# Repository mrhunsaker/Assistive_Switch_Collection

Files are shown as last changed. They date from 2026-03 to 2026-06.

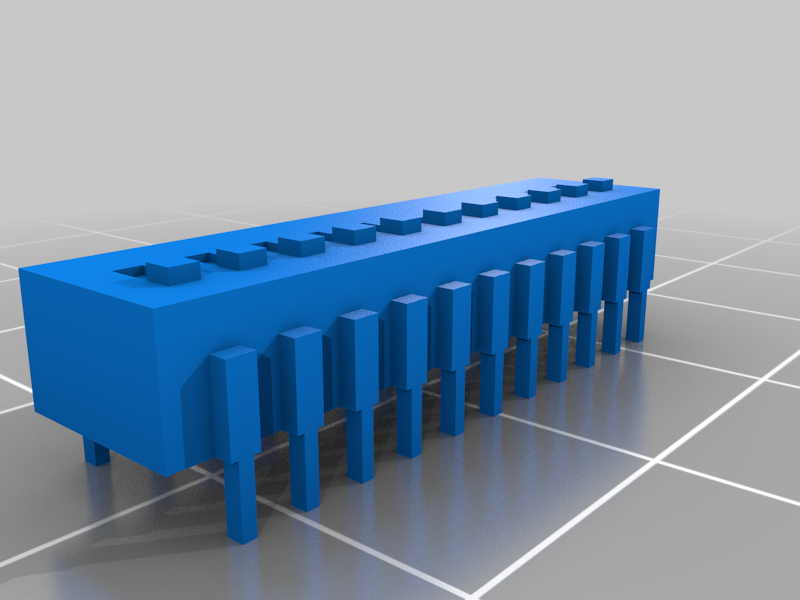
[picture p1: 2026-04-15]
TOSORT/DIP SWITCH, PUSH BUTTON, LED ELECTRONICS STL SPACE MODELS - 806060/images/2058_DIP_SWITCH.png

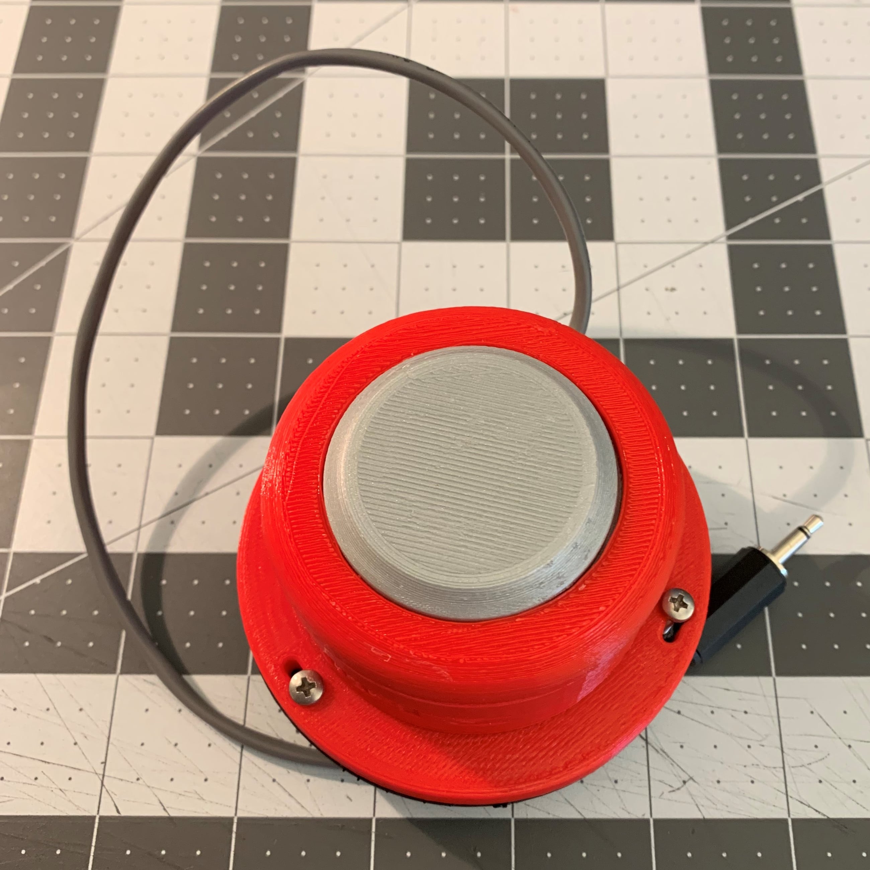
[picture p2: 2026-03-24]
switches/atmakers/AT Switch Remix - 3583410/images/Print_Assembled.jpg

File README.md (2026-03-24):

# Assistive Switch Collection

This repository is a curated collection of open‑source assistive **switches** and **switch interfaces**, collected as Git submodules and indexed in a machine‑readable CSV file.

The goal is to make it easier for clinicians, AT professionals, and makers to discover, compare, and build on existing open hardware.

---

## Repository structure

- `switch_projects.csv` — master index of projects (name, repo URL, type, number of inputs, IO mode, license, and whether 3D models are available).  
- `repos/` — Git submodules pointing at each upstream project.  
- `docs/` (optional) — any generated site or additional documentation.

---

## Project metadata fields

Each row in `switch_projects.csv` uses the following columns:

- `name` — human‑readable project name.  
- `github_repo` — canonical repository URL or project page if the code is linked from there.  
- `type` — one of:
  - `switch` for physical access switches (typically 3.5 mm).  
  - `interface` for devices that turn one or more switches (or sip‑and‑puff) into USB HID, gamepad, network, or relay outputs.  
  - `switch_controlled_device` for projects where the main goal is controlling something else (e.g., coffee maker, water pump) with an assistive switch.  
- `inputs` — approximate number and type of user inputs (e.g., `1`, `2`, `2+ sip_puff`).  
- `io_mode` — how the device presents itself or actuates:
  - `USB_HID`, `Bluetooth_HID`, `relay`, `network_to_servo`, `contact_closure`, etc.  
- `license` — SPDX identifier or short description (e.g., `MIT`, `CC-BY-NC-SA 4.0`).  
- `has_3d_files` — `yes` / `no` / `unknown`.  
- `notes` — brief free‑text description, special features, or caveats (e.g., non‑commercial license, requires specific microcontroller).

---

## Adding a new project

1. **Add the submodule**

   ```bash
   git submodule add https://github.com/USER/REPO.git repos/REPO
<!-- SUBMODULES:START -- auto-generated by add_submodules.sh, do not edit this block manually -->
## Submodules

This repository contains **48** submodule(s) organized by source.

To initialize after cloning:

```bash
git submodule update --init --recursive
```

### MMC: Physical Switches

| Repository | Path | Description |
|---|---|---|
| [`Chatterbox`](https://github.com/makersmakingchange/Chatterbox.git) | `switches/mmc/Chatterbox` | A switch scanning AAC device for users with visual impairment. |
| [`Lift-Switch`](https://github.com/makersmakingchange/Lift-Switch.git) | `switches/mmc/Lift-Switch` | A Switch Modifier that enables a switch to be activated when the switch is released rather than when pressed. |
| [`MMC60_Assistive_Switch`](https://github.com/makersmakingchange/MMC60_Assistive_Switch.git) | `switches/mmc/MMC60_Assistive_Switch` | A robust, 3D printable assistive switch with a 3.5 mm cable and easily swappable tops. |
| [`Twitch-Switch`](https://github.com/makersmakingchange/Twitch-Switch.git) | `switches/mmc/Twitch-Switch` | The Twitch Switch allows you to activate up to 3 switch adapted devices, or emulate a mouse or keyboard with movement as subtle as twitching your eyebrow. |
| [`Light-Proximity-Switch`](https://github.com/makersmakingchange/Light-Proximity-Switch.git) | `switches/mmc/Light-Proximity-Switch` | An open-source assistive switch that is activated by movement or extremely light contact. |
| [`Open-Wobble-Switch`](https://github.com/makersmakingchange/Open-Wobble-Switch.git) | `switches/mmc/Open-Wobble-Switch` | A cost effective wobble switch. This mountable assistive switch can be activated by moving the wand in any direction. |
| [`Interact-Switch`](https://github.com/makersmakingchange/Interact-Switch.git) | `switches/mmc/Interact-Switch` | An open source, 3D printable assistive switch with multiple topper options. |
| [`Big_Open_Switch`](https://github.com/makersmakingchange/Big_Open_Switch.git) | `switches/mmc/Big_Open_Switch` | A 3D printable assistive switch with a diameter of 150 mm |
| [`foot-pedal-switch`](https://github.com/makersmakingchange/foot-pedal-switch.git) | `switches/mmc/foot-pedal-switch` | A modified commercial foot pedal switch for use as an assistive switch |
| [`Open-Rocker-Switch`](https://github.com/makersmakingchange/Open-Rocker-Switch.git) | `switches/mmc/Open-Rocker-Switch` | An open source assistive switch activated by pressing down on either side or rocking the top relative to the base. |
| [`Round_Touch_60_Switch`](https://github.com/makersmakingchange/Round_Touch_60_Switch.git) | `switches/mmc/Round_Touch_60_Switch` | The Round Touch 60 Switch can control 3.5 mm audio outputs like in the Xbox Adaptive Controller and other switch adapted products.  |
| [`Raindrop-Switch`](https://github.com/makersmakingchange/Raindrop-Switch.git) | `switches/mmc/Raindrop-Switch` | A small, pressure-activated assistive switch |
| [`Resistive-Touch-Switch`](https://github.com/makersmakingchange/Resistive-Touch-Switch.git) | `switches/mmc/Resistive-Touch-Switch` | An open source assistive switch activated by minimal force skin contact. |
| [`Light-Touch-Switch`](https://github.com/makersmakingchange/Light-Touch-Switch.git) | `switches/mmc/Light-Touch-Switch` | A slim, pressure activated assistive switch with a 3.5 mm connection. |
| [`Wearable-Clap-Switch`](https://github.com/makersmakingchange/Wearable-Clap-Switch.git) | `switches/mmc/Wearable-Clap-Switch` | A wearable wireless switch that detects clap motion and activates an assistive device. |
| [`Finger-Lift-Switch`](https://github.com/makersmakingchange/Finger-Lift-Switch.git) | `switches/mmc/Finger-Lift-Switch` | An open-source assistive switch that can be activated by small lifting motions of a finger. |
| [`Hand-Raiser`](https://github.com/makersmakingchange/Hand-Raiser.git) | `switches/mmc/Hand-Raiser` | An assistive device used to catch the attention of a professor: an alternative to a student having to raise their hand. |
| [`Low-Profile-Switch`](https://github.com/makersmakingchange/Low-Profile-Switch.git) | `switches/mmc/Low-Profile-Switch` | A 3D printable, low profile assistive switch |
| [`Solderless-Unibody-Switch`](https://github.com/makersmakingchange/Solderless-Unibody-Switch.git) | `switches/mmc/Solderless-Unibody-Switch` | A solderless unibody assistive switch |
| [`Assistive-Switches-Kit`](https://github.com/makersmakingchange/Assistive-Switches-Kit.git) | `switches/mmc/Assistive-Switches-Kit` | An assortment of DIY 3d printable assistive switches. |
| [`Sip-And-Puff-Analog-Switch`](https://github.com/makersmakingchange/Sip-And-Puff-Analog-Switch.git) | `switches/mmc/Sip-And-Puff-Analog-Switch` | An open source analog sip and puff assistive switch |

### MMC: Switch Modifiers / Adapters

| Repository | Path | Description |
|---|---|---|
| [`Switch-Modifier`](https://github.com/makersmakingchange/Switch-Modifier.git) | `switches/mmc/Switch-Modifier` | An open assistive technology for modifying the output of an assistive switch |
| [`OpenAT-Switch-Latch`](https://github.com/makersmakingchange/OpenAT-Switch-Latch.git) | `switches/mmc/OpenAT-Switch-Latch` | An Open Assistive Technology device that adds latching functionality to an assistive switch. |
| [`Switch-Adapter-DualMono-Stereo`](https://github.com/makersmakingchange/Switch-Adapter-DualMono-Stereo.git) | `switches/mmc/Switch-Adapter-DualMono-Stereo` | Adapter for connecting two assistive switches to a single stereo input. |

### MMC: Switch Interfaces / Testers

| Repository | Path | Description |
|---|---|---|
| [`USB-Switch-Tester`](https://github.com/makersmakingchange/USB-Switch-Tester.git) | `switches/mmc/USB-Switch-Tester` | A DIY open source hardware device to test if an assistive switch is functional. |
| [`Simple-Switch-Tester`](https://github.com/makersmakingchange/Simple-Switch-Tester.git) | `switches/mmc/Simple-Switch-Tester` | A simple battery operated tester with a light for testing assistive switches via a 3.5 mm jack. |
| [`Shrub-Hub`](https://github.com/makersmakingchange/Shrub-Hub.git) | `switches/mmc/Shrub-Hub` | A low cost, easy to build digital switch interface for up to three assistive switches |
| [`Trinkey-Assistive-Interface`](https://github.com/makersmakingchange/Trinkey-Assistive-Interface.git) | `switches/mmc/Trinkey-Assistive-Interface` | A simple to build cost-effective assistive interface for digital access based on the Adafruit TRRS Trinkey. |
| [`Playback-Switch`](https://github.com/makersmakingchange/Playback-Switch.git) | `switches/mmc/Playback-Switch` | The Playback Switch is an assistive switch that also plays a prerecorded message up to 30 seconds long when the button is pressed.  |
| [`Single-Message-Playback-Switch`](https://github.com/makersmakingchange/Single-Message-Playback-Switch.git) | `switches/mmc/Single-Message-Playback-Switch` | Guide for modifying commercial message playback to work with external assistive switch. |
| [`Rocket-Switch-Interface`](https://github.com/makersmakingchange/Rocket-Switch-Interface.git) | `switches/mmc/Rocket-Switch-Interface` | A cost-effective two input switch interface based on a commercially available Trinkey board. |

### MMC: Wireless

| Repository | Path | Description |
|---|---|---|
| [`Wireless-Assistive-Swith-Link`](https://github.com/makersmakingchange/Wireless-Assistive-Swith-Link.git) | `switches/mmc/Wireless-Assistive-Switch-Link` | A wireless link between a 3.5 mm switch and an output device that has a 3.5 mm jack |
| [`wireless-assistive-switch-link`](https://github.com/makersmakingchange/wireless-assistive-switch-link.git) | `switches/mmc/wireless-assistive-switch-link` | Provides a way to wirelessly connect an assistive switch to a switch-adapted output device. |

### MMC: Mounting / Accessories

| Repository | Path | Description |
|---|---|---|
| [`Open_Universal_Mounting_Plate`](https://github.com/makersmakingchange/Open_Universal_Mounting_Plate.git) | `switches/mmc/Open_Universal_Mounting_Plate` | A simple 3d printed mount for assistive technology. Provides a flat surface for attaching AT using hook and loop fastener. Has a 1/4-20 UNC for compatibility with camera mounting options. |
| [`USB-Switcher-Modification`](https://github.com/makersmakingchange/USB-Switcher-Modification.git) | `switches/mmc/USB-Switcher-Modification` | This is a modification adds a switch jack input to the commercially available Sabrent USB 2.0 Sharing Switch, a device that allows a person to connect one USB device to two computers and switch between them. |
| [`Custom-Single-Switch-Kit`](https://github.com/makersmakingchange/Custom-Single-Switch-Kit.git) | `switches/mmc/Custom-Single-Switch-Kit` | An assistive switch that uses heat moldable polymer for a customized fit. |

### MMC: Sip-and-Puff Joysticks

| Repository | Path | Description |
|---|---|---|
| [`LipSync`](https://github.com/makersmakingchange/LipSync.git) | `switches/mmc/LipSync` | An open-source mouth operated sip and puff joystick that enables people with limited hand function to emulate a mouse on their computer and/or smartphone. |
| [`LipSync-Macro`](https://github.com/makersmakingchange/LipSync-Macro.git) | `switches/mmc/LipSync-Macro` | A mouth controlled open assistive technology alternative input device. |

### AsTeRICS

| Repository | Path | Description |
|---|---|---|
| [`buttondesigns`](https://github.com/asterics/buttondesigns) | `switches/asterics/buttondesigns` | Various 3D printed switch acuators for assistive input |
| [`FLipMouse`](https://github.com/asterics/FLipMouse) | `switches/asterics/FLipMouse` | The repository for FLipMouse (Finger and LipMouse) |
| [`FLipMouse-v2`](https://github.com/asterics/FLipMouse-v2) | `switches/asterics/FLipMouse-v2` | FLipMouse Version 2 |
| [`FABI`](https://github.com/asterics/FABI) | `switches/asterics/FABI` | The repository for FABI (Flexible Assistive Button Interface) |

### MTurvey

| Repository | Path | Description |
|---|---|---|
| [`InteractSwitch`](https://github.com/mwturvey/InteractSwitch.git) | `switches/mturvey/InteractSwitch` | Designs for a set of assistive technology switches |

### Misc / Community

| Repository | Path | Description |
|---|---|---|
| [`accessible-switches`](https://github.com/a11yhood/accessible-switches) | `switches/misc/accessible-switches` |  |
| [`Accessible-Switch`](https://github.com/greenpanda111/Accessible-Switch) | `switches/misc/Accessible-Switch` | CAD files to construct an accessible switch |
| [`atat-switch`](https://github.com/musghz/atat-switch) | `switches/misc/atat-switch` | Open source accessibility switch based on mechanical keyboard switches |
| [`openSipPuff`](https://github.com/jasonwebb/openSipPuff) | `switches/misc/openSipPuff` | Simple, low-cost \ |
| [`Sip-N-Puff-Accessibility-Project`](https://github.com/trainslaw/Sip-N-Puff-Accessibility-Project) | `switches/misc/Sip-N-Puff-Accessibility-Project` |  |

<!-- SUBMODULES:END -->

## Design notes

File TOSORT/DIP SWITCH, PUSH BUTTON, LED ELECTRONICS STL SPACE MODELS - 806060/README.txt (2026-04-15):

DIP SWITCH, PUSH BUTTON, LED ELECTRONICS STL SPACE MODELS by bathrobotics on Thingiverse: https://www.thingiverse.com/thing:806060

Summary:
THESE ARE ACCURATE FOR THE PURPOSES I USE.  FEEL FREE TO DOWNLOAD THE .PK2 CREO ELEMENTS FILE AND MODIFY FOR YOUR NEEDS.  10 WAY DUAL INLINE SWITCH,  LED WITH LEGS,  PUSH BUTTON

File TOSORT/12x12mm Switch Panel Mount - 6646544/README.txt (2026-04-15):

12x12mm Switch Panel Mount by TuriSc on Thingiverse: https://www.thingiverse.com/thing:6646544

Summary:
This enclosure is designed for mounting standard 12x12mm tactile micro switches to panels.It requires a 20mm hole for installation.After inserting the switch with its cap on, attach the locking part to secure it in place.The design does not require any supports for printing.

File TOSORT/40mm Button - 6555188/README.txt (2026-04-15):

40mm Button by paedia on Thingiverse: https://www.thingiverse.com/thing:6555188

Summary:
Sturdy 40mm Button. The clever scissor mechanism evenly distributes the pressure across the entire contact surface. The built-in microswitch is reliably activated even when pressed in the corner. The button is very robust and can also be used as a foot switch.Assembly: First, snap the scissor parts onto the base, then insert the microswitch and snap on the cover.Additionally, you’ll need:1 standard 5A microswitch (Omron SS-5 F or similar)2 brass inserts (M3, 5mm)2 countersunk screws (M3, 6mm)

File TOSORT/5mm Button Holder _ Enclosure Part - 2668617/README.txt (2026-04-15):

5mm Button Holder / Enclosure Part by PrintedHuman on Thingiverse: https://www.thingiverse.com/thing:2668617

Summary:
Need to include buttons in your project or model? Just paste in this model and you are ready.This is the optimized result of testing and prototypes and it fits like a charm with the usual cheap 5 mm switch push buttons.You don't need to give credit if you use this part, but I would thank you if you did, just link to this page. Thanks!There are 2 models, one with and one without a seperator. The seperator is useful for making sure that solder or wires wont short circuit with eachother.Enjoy!PS. You can buy this buttons safely and cheap over here: https://www.banggood.com/100pcs-Mini-Micro-Momentary-Tactile-Tact-Switch-Push-Button-DIP-P4-Normally-Open-p-917570.html?p=BE271351829962016060(Those are also the buttons I used for prototyping and testing)

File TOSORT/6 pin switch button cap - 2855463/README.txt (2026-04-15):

6 pin switch button cap by matszwe02 on Thingiverse: https://www.thingiverse.com/thing:2855463

Summary:
This is a simple power switch cap

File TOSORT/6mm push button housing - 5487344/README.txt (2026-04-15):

6mm push button housing by ringo2k on Thingiverse: https://www.thingiverse.com/thing:5487344

Summary:
This is an enclosure for a 6mmx6mm push button. I like the cheap buttons because of the the nice "push feeling". I wanted to have a base, which I can use to put these buttons on electronics housings. You need to print 3 parts: The base - There you put in the button (bend the legs and solder cables to it upfront)The pin - This is the pin, place it on the buttonThe housing - Put everything in the housing (super glue it together)That's it!

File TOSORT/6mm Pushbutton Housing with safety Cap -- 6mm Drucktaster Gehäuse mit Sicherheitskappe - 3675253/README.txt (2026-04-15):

6mm Pushbutton Housing with safety Cap  --  6mm Drucktaster Gehäuse mit Sicherheitskappe by SolarGermany on Thingiverse: https://www.thingiverse.com/thing:3675253

Summary:
6mm Pushbutton Housing with safety Caphttps://www.ebay.de/itm/100PCS-6x6x6-mm-Miniature-Micro-Momentary-Tactile-Tact-Touch-Push-Button-Switch/132488686881?epid=633717124&amp;hash=item1ed8f0ed21:g:7DIAAOSwWlFbrzqw&amp;frcectupt=trueHave fun, like, and share you makes...SG.-.-.-.-.-.-.-.-.-.-.-.-.-.-.-.-.-.-.-.-.-.-.-.-.-.-.-.-.-.-.-.-.-.-.-.-.-.-.-.-.-.-.-.-.-.-.-.-.-.-.-.-.-.-.-.-.-.-.-.-.-.-.-.-.-.6mm Drucktaster Gehäuse mit Sicherheitskappehttps://www.ebay.de/itm/100PCS-6x6x6-mm-Miniature-Micro-Momentary-Tactile-Tact-Touch-Push-Button-Switch/132488686881?epid=633717124&amp;hash=item1ed8f0ed21:g:7DIAAOSwWlFbrzqw&amp;frcectupt=trueHabt Spass, liked, und teilt Eure Makes...SG

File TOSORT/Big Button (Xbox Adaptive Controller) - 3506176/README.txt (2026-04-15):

Big Button (Xbox Adaptive Controller) by gripuf on Thingiverse: https://www.thingiverse.com/thing:3506176

Summary:
This design is a big button for use with the Xbox Adaptive Controller (XAC). The part is made up of 3 seperate components: the top of the button case, the bottom of the button case, and the actual button that you press. These components are all available for download as stl and SolidWorks files. On the inside of the part, there is a square slota to hold a keyboard switch. We used Green Cherry MX Keyswitches (https://mechanicalkeyboards.com/shop/index.php?l=product_list&amp;c=48) so those will fit best into the square slot.We use zipties to secure the top and base of the switch together.

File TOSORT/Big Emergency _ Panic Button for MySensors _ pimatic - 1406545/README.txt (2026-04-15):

Big Emergency / Panic Button for MySensors / pimatic by MaxWinterstein on Thingiverse: https://www.thingiverse.com/thing:1406545

Summary:
Emergency Button This is some big Emergency Button. I use it with my HouseAutomation to control things and stuff. As button itself i use a black Cherry MX switch that i had laying around. Works nice :)When it was printed i thought a lower height would be great, so i added a 15mm/piece version. The version in the video is 30mm/piece.What you need to do it like me:all three printed partsCherry MX switch of your choice (i got mine from Conrad GermanyArduino NRF24L01+ Radiosome cablessome M3 Screws (M3x30+ should do fine)You can read more about that stuff here:Software i use pimatic.orgHardware i use mysensors.orgVideo: https://www.youtube.com/watch?v=jMr5voq1hkAI stole the idea for fixing the knob to the switch from ohagel. Thanks buddy, mine creation did not work as expected ;)Update v2I changed the plate thickness of the top part from 1mm to 1.5mm, that should make the Cherry Switch fit much better.Update v3I think using one cherry switch is great. But using 4 cherry switches is even four times greater. So i added a top and a knob that can handle 4 cherry switches. I made one, and it feels very good. Sadly yellow is empty, so mine is gray.Update v4Added CAD files. Please be nice, i am not that good at it.

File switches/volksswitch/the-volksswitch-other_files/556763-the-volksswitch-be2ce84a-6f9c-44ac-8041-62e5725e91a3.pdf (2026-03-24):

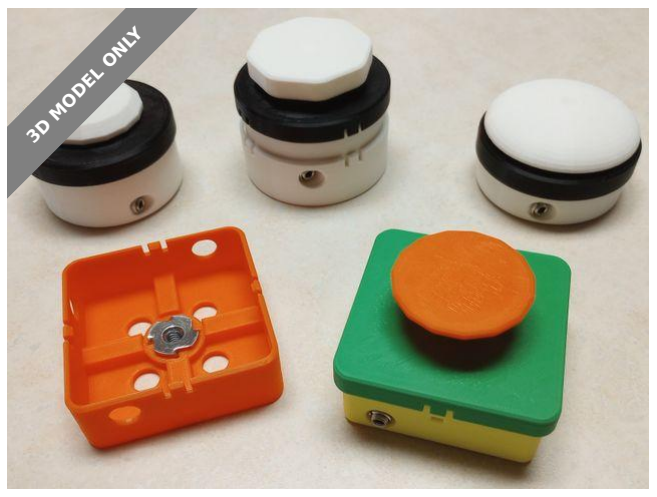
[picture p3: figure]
3D MODEL ONLY

## Summary

This pressure switch designer is highly customizable and requires no

soldering to assemble.

Hobby & Makers (https://printables.com/model?categoryId=48) | > | Electronics (https://printables.com/model?categoryId=52)
Tags: switch | customizable | assistivetech | assistivetechnology

This pressure switch designer allows you to customize the switch size,

shape, activation distance, activation force, and activation location. In

addition to a 3D-printed enclosure and activation surface, it uses off-the-

shelf parts that can be assembled using only a screwdriver. No Soldering

Necessary!

Instructions for using the switch designer can be found at the

Volksswitch.org website on this page:

https://volksswitch.org/index.php/volks-devices/the-volksswitch/

Volksswitch (https://printables.com/@Volksswitch_273749)

# The Volksswitch

VIEW IN BROWSER (https://printables.com/model/556763-the-volksswitch)

updated 26. 9. 2023 | published 26. 9. 2023

# Model files

# Other files

- remove the .txt part of the file name before expanding into a folder

## License

This work is licensed under a

Creative Commons (4.0 International License)

Attribution (http://creativecommons.org/licenses/by/4.0/)

✖ | Sharing without ATTRIBUTION
✔ | Remix Culture allowed
✔ | Commercial Use
✔ | Free Cultural Works
✔ | Meets Open Definition

the-volksswitch.scad

spacer-plug-matrix.pdf

evaluation_switch_stl_fileszip.txt

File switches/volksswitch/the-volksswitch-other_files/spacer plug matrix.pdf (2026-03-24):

activation force index | activation distance
0 | 1 | 2 | 3 | 4 | 5
0 | ?*
1 | 3.5 | 4.5 | 5.5 | 6.5 | 7.5 | 8.5
2 | 3.5 | 4.5 | 5.5 | 6.5 | 7.5 | 8.5
3 | 3 | 4 | 5 | 6 | 7 | 8
4 | 3 | 3.5 | 4.5 | 5.5 | 6.5 | 7.5
5 | 3 | 4 | 5 | 6 | 7 | 8
6 | 3 | 3 | 4 | 5 | 6 | 7
7 | 3 | 3.5 | 4.5 | 5.5 | 6.5 | 7.5
8 | 3 | 3 | 3.5 | 4.5 | 5.5 | 6.5
9 | 3 | 3 | 4 | 5 | 6 | 7
10 | 3 | 3 | 3.5 | 4.5 | 5.5 | 6.5
? = 6 for evaluation switches and 3 for standard switches
* = insert mini-post

not available
not available for 10 mm spacer

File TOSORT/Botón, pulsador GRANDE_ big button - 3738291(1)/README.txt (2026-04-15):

Botón, pulsador GRANDE/ big button by lafabricadepalabras on Thingiverse: https://www.thingiverse.com/thing:3738291

Summary:
Pulsador  (no interruptor)  de grandes dimensiones diseñado especialmente para personas con diversidad funcional. A éste se le conecta un cable jack para poder gobernar juguetes adaptados, dispositivos que faciliten el barrido en comunicadores, etc. Gracias a la gran labor de CEAPAT, con el diseño:https://www.thingiverse.com/thing:1096831

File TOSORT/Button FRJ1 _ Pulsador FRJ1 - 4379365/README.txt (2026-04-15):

Button FRJ1 / Pulsador FRJ1 by ceapat on Thingiverse: https://www.thingiverse.com/thing:4379365

Summary:
Switch designed for people with limited movement to operate communication equipment, toys and other electronic equipment.[Spanish] Pulsador doble de fácil accionamiento, para facilitar el acceso a otros productos adaptados para personas con movilidad reducida.Se puede utilizar con juguetes adaptados, mandos de TV, ratones y otros productos electrónicos adaptados.

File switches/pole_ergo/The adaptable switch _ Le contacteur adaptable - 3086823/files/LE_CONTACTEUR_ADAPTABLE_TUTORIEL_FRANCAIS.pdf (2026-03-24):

CC BY-NC-SA pole-ergo.fr - Guy Ehretsmann | 2018
www.pole-ergo.fr | technologie@pole-ergo.fr

LE CONTACTEUR ADAPTABLE

Guy Ehretsmann/Ergothérapeute

INTRODUCTION

Le contacteur est un bouton poussoir accessible très utilisé dans le domaine du handicap. Il est conçu pour faciliter l'accès à différents types de technologies et, de façon étendue, pour permettre à l'utilisateur d'agir sur son environnement.

Il transforme un geste moteur, manquant de précision, en, par exemple, un signal exploitable par un ordinateur, une tablette ou un téléphone pour les contrôler intégralement lorsqu'ils sont paramétrés pour ce mode de fonctionnement.

Le contacteur donne également l'accès à des jouets électriques, à des dispositifs de communications ou encore à des appareils pilotés par boutons tel que appareils photos, console de jeux, etc..

Les contacteurs sont disponibles dans le commerce spécialisé. On en trouve ainsi de différentes tailles, couleurs mais également de différents types et formes. Pourtant, le contacteur peut se révéler difficile à utiliser lorsque son design ne correspond pas au besoins spécifiques de l'utilisateur.

C'est la raison pour laquelle il peut s'avérer pertinent de disposer d'un contacteur adaptable que l'on pourra modifier en fonction des particularités motrices de l'utilisateur, de ses habitudes ou encore de ses goûts de façon à le rendre davantage accessible.

Le contacteur adaptable proposé ici offre une série de possibilités et d'options de personnalisations qui le rende potentiellement capable de répondre à toutes les situations.

Totalement imprimé à l'aide d'une imprimante 3D, les différentes pièces qui le composent s'assemblent comme des briques de Lego. Il offre différentes possibilités de fixations et de positionnement en exploitant la norme utilisée pour les minis caméras GOPRO, dont on trouve partout les accessoires à bas prix.

Il dispose également d'un bouton spécifique comportant des fixations à vis qui permet la fabrication et l'usage de boutons personnalisés et constitue, ainsi, une base pour la création de modèles uniques répondant à des besoins non génériques.

Enfin, l'assemblage du contacteur est facile et ne demande que deux soudures simples à l'étain qu'il est possible d'éviter, lorsque l'on ne dispose pas de fer à souder, en réalisant un simple sertissage de fils.

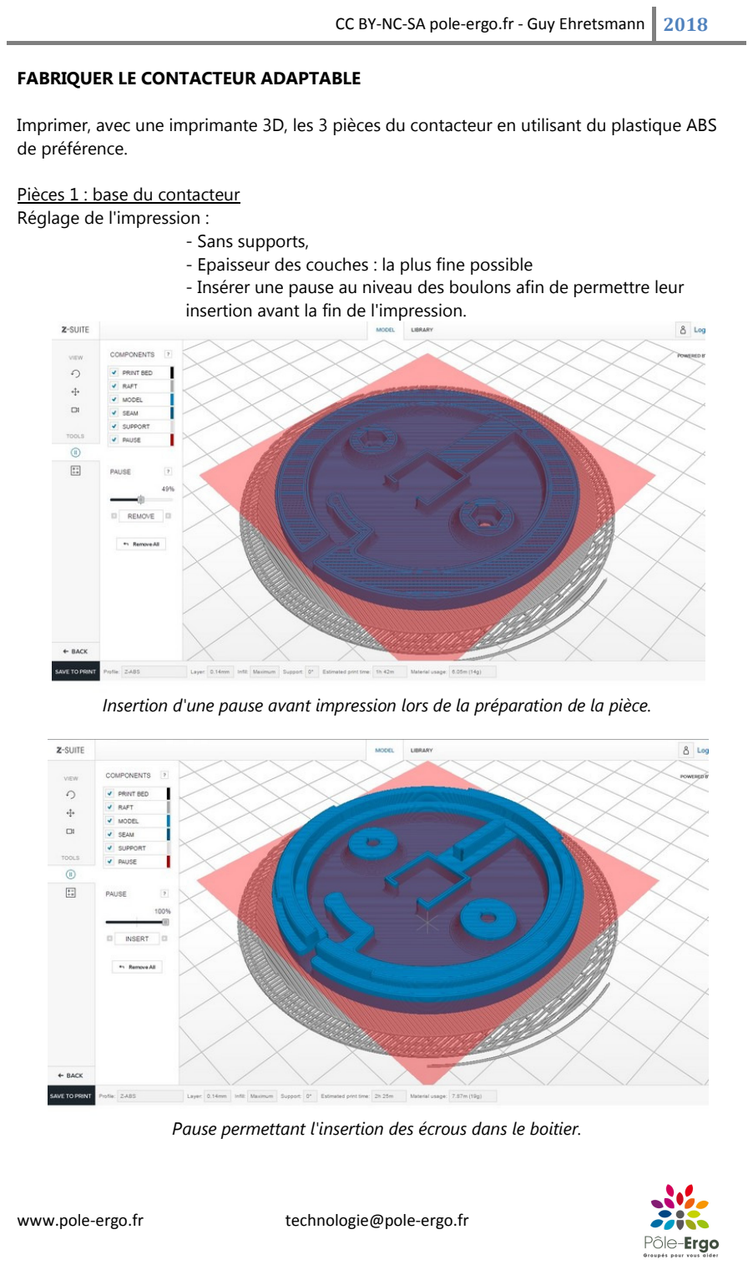
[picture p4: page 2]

FABRIQUER LE CONTACTEUR ADAPTABLE

Imprimer, avec une imprimante 3D, les 3 pièces du contacteur en utilisant du plastique ABS de préférence.

Pièces 1 : base du contacteur
Réglage de l'impression :
- Sans supports,
- Epaisseur des couches : la plus fine possible
- Insérer une pause au niveau des boulons afin de permettre leur insertion avant la fin de l'impression.

Insertion d'une pause avant impression lors de la préparation de la pièce.

Pause permettant l'insertion des écrous dans le boitier.

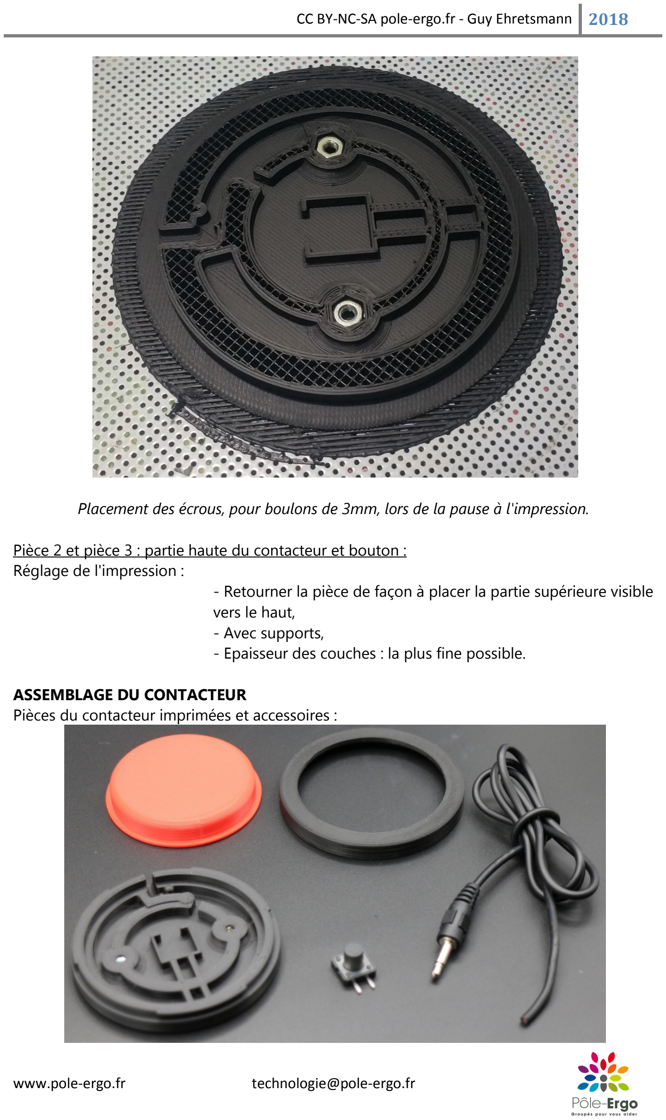
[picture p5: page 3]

Placement des écrous, pour boulons de 3mm, lors de la pause à l'impression.

Pièce 2 et pièce 3 : partie haute du contacteur et bouton : Réglage de l'impression :
- Retourner la pièce de façon à placer la partie supérieure visible vers le haut,
- Avec supports,
- Epaisseur des couches : la plus fine possible.

ASSEMBLAGE DU CONTACTEUR
Pièces du contacteur imprimées et accessoires :

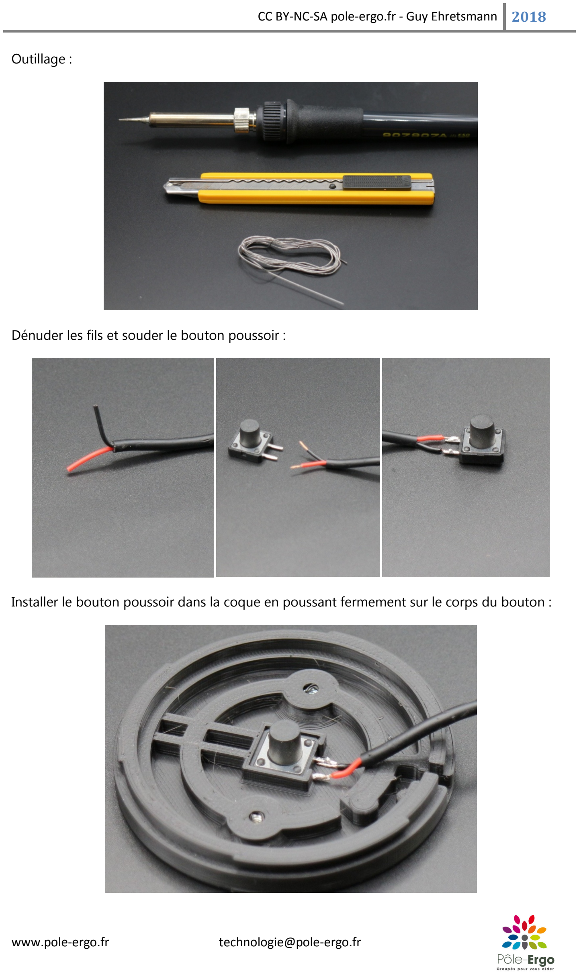
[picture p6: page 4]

Outillage :

Dénuder les fils et souder le bouton poussoir :

Installer le bouton poussoir dans la coque en poussant fermement sur le corps du bouton :

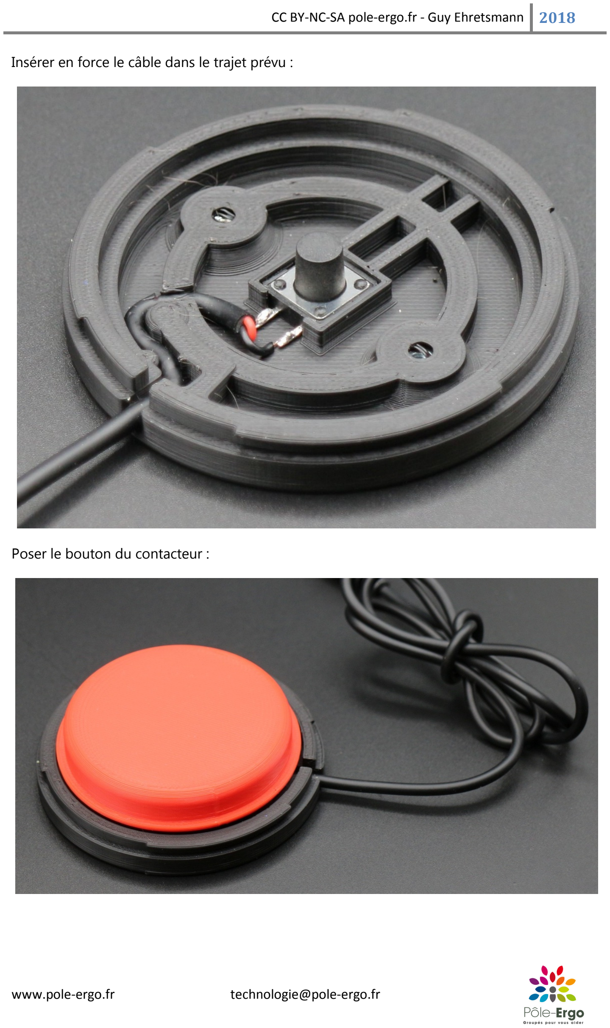
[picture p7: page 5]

Insérer en force le câble dans le trajet prévu :

Poser le bouton du contacteur :

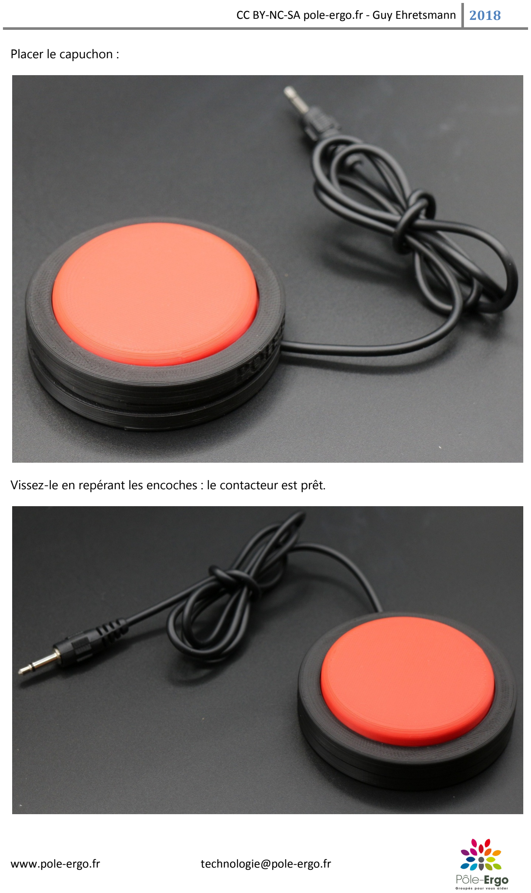
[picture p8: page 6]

Placer le capuchon :

Vissez-le en repérant les encoches : le contacteur est prêt.

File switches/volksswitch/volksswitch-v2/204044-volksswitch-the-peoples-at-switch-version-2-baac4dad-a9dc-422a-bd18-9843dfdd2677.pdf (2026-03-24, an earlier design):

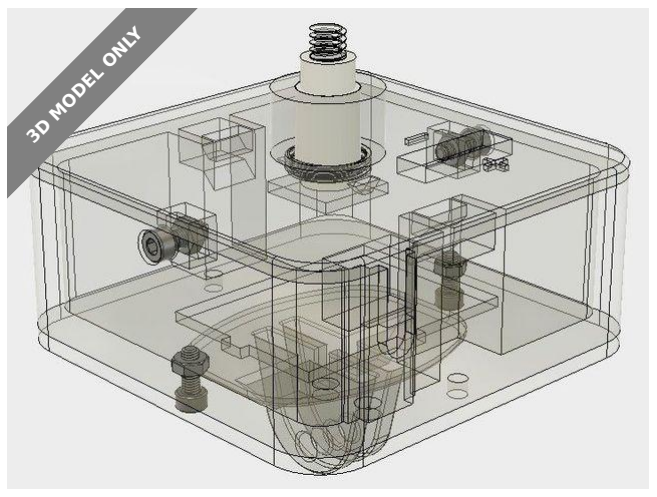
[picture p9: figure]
3D MODEL ONLY

## Summary

With this remix we removed the need for the heat-set threaded inserts to attach the cover and GoPro mount to the base....

Hobby & Makers (https://www.printables.com/model?categoryId=48) > Other Ideas (https://www.printables.com/model?categoryId=82)

Tags: assistivetech | assistivetechnology | assistivedevice

With this remix we removed the need for the heat-set threaded inserts to attach the cover and GoPro mount to the base. These components are expensive and take special equipment to insert them into the base and activation surface. We also replaced the 1/4 inch bolt with a printed post and a screw-in collar (with its own Teflon tube lining) to make the connection between the activation surface and the internal spring more stable and the action smoother. Because the post has to be printed vertically, it is sensitive to horizontal stresses. You may want to use a 1-1/4′′ x 1/4′′ hex head bolt for greater strength, instead.

Download the files and then go to my website at: https://wp.me/P9evBA-4D (https://wp.me/P9evBA-4D) to learn more about additional parts that are needed and how to assemble everything. If you're interested in helping to improve on the design of the Volksswitch go here (https://wp.me/P9evBA-7) and provide your contact information.

Volksswitch (https://www.printables.com/social/273749/about)

## Volksswitch - the

## People's AT Switch

## (Version 2)

VIEW IN BROWSER (https://www.printables.com/model/204044-volksswitch-the-peoples-at-switch-version-2)

updated 13. 5. 2022 | published 13. 5. 2022

## Model files

Print Settings

Printer Brand:

Prusa

Printer:

i3 MK3

Rafts:

No

Supports:

No

Resolution:

0.1 mm

Infill:

20%

Notes:

print the post with additional perimeters and 100% infill to make it as strong as possible.

Post-Printing

Download the files and then go to my website at: https://wp.me/P9evBA-4D (https://wp.me/P9evBA-4D) to learn more about additional parts that are needed and how to assemble everything.

Category: Other

post_204044.stl

Find source .stl files on Thingiverse.com (https://www.thingiverse.com/thing:2870415)

## License

This work is licensed under a
Creative Commons (4.0 International License)

Attribution (http://creativecommons.org/licenses/by/4.0/)

collar_204044.stl

base_204044.stl

square_activation_surface_-_no_insert_204044.stl

cover_204044.stl

gopro_mount_204044.stl

collar_bigger_hole_204044.stl

round_activation_surface_-_no_insert_204044.stl

✖ | Sharing without ATTRIBUTION
✔ | Remix Culture allowed
✔ | Commercial Use
✔ | Free Cultural Works
✔ | Meets Open Definition

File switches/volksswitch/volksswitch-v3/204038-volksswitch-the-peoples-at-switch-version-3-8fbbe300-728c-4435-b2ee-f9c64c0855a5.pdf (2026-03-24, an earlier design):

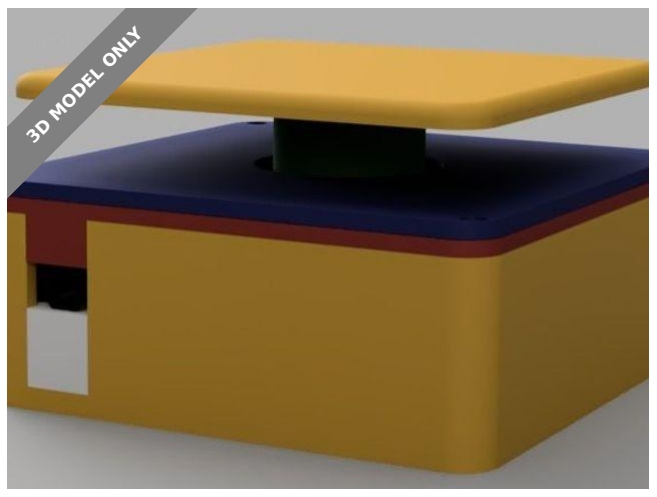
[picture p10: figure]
3D MODEL ONLY

# Summary

This remix is in homage to the "flexure bearing". I don't know why it's

called a bearing. I prefer to think of it as a...

Hobby & Makers (https://www.printables.com/model?categoryId=48) | > | Other Ideas (https://www.printables.com/model?categoryId=82)
Tags: assistivetech | assistivetechnology | assistivedevice

This remix is in homage to the "flexure bearing". I don't know why it's

called a bearing. I prefer to think of it as a flexure "spring". I first became

aware of this concept when I looked at Drew Browning's switch "DIYAT

Switch V5 (microswitch, radial flexures)".

It occurred to me that a flexure spring design could solve many of the

problems that I've encountered in trying to design a 3D printable, button

switch:

- it's hard to find a commercial spring that is just the right length, just the

right diameter and just the right stiffness - it's so much better if you can

3D print the spring to your specification

- many button switch designs place a collar around the button in order to

provide stability but the button inevitably rubs against the collar when

depressed causing a scraping sound and feel - with a flexure spring the

button sits stable on the spring, a collar isn't even necessary.

Volksswitch (https://www.printables.com/social/273749/about)

# Volksswitch - the

# People's AT Switch

# (Version 3)

VIEW IN BROWSER (https://www.printables.com/model/204038-volksswitch-the-peoples-at-switch-version-3)

updated 13. 5. 2022 | published 13. 5. 2022

# Model files

- buttons that sit on traditional coil springs can wobble from side to side

and can even get caught under their collar once depressed - a flexure

spring works to keep the movement of the button mostly vertical and

causes the button to right itself quickly once released

Download the files and then go to my website at: http://volksswitch.org/

index.php/volks-devices/volksswitch-proof-of-concept/volksswitch-remixes/

23-december-2018-mechanical-remix/ (http://volksswitch.org/index.php/volks-devices/volksswitch-proof-of-concept/volksswitch-remixes/23-december-2018-mechanical-remix/) to learn more about additional parts

that are needed and how to assemble everything. If you're interested in

helping to improve on the design of the Volksswitch go here (https://

wp.me/P9evBA-7) and provide your contact information.

Category: Other

cover_204038.stl

## base_204038.stl

## post_204038.stl

flat_activation_surface_204038.stl

linear_arm_flexure_spring_204038.stl

activation_surface_mount_204038.stl

Find source .stl files on Thingiverse.com (https://www.thingiverse.com/thing:3310067)

# License

This work is licensed under a

Creative Commons (4.0 International License)

Attribution (http://creativecommons.org/licenses/by/4.0/)

### ✖ | Sharing without ATTRIBUTION

✔ | Remix Culture allowed
✔ | Commercial Use
✔ | Free Cultural Works
✔ | Meets Open Definition

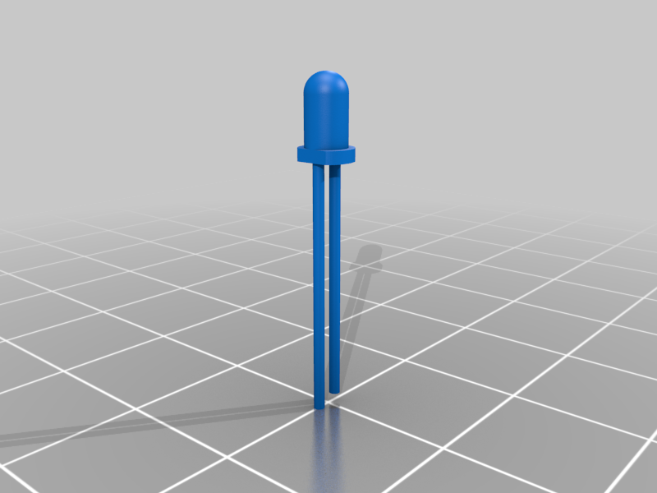
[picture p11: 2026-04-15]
TOSORT/DIP SWITCH, PUSH BUTTON, LED ELECTRONICS STL SPACE MODELS - 806060/images/2060_PUSH_BUTTON.png

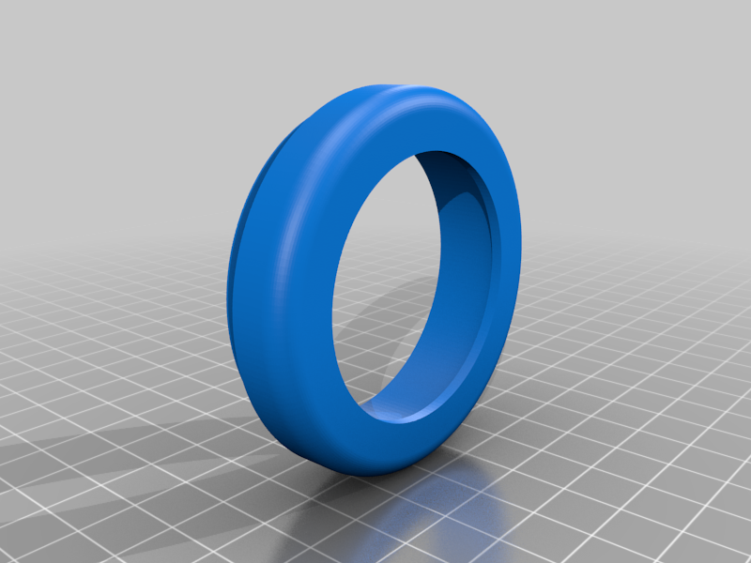
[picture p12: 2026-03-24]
switches/misc/Modified AT Switch Design - 2507266/images/320979af08b27aef6b695a60599e2505.png

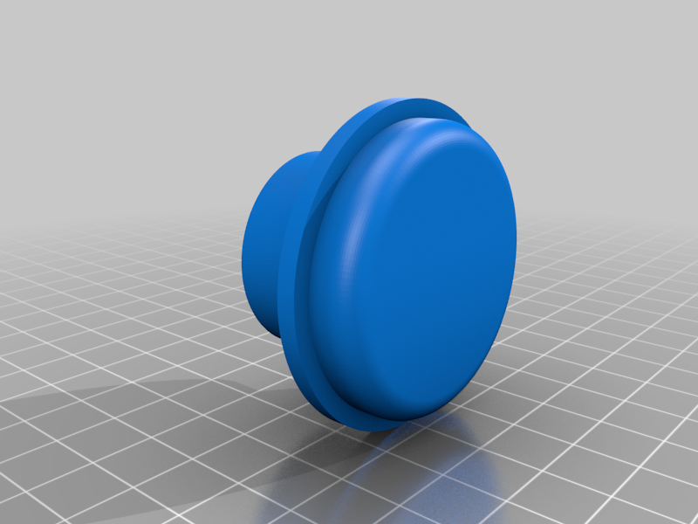
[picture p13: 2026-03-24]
switches/misc/Modified AT Switch Design - 2507266/images/fd9e4b077ecdf45762ce9707d49869b7.png

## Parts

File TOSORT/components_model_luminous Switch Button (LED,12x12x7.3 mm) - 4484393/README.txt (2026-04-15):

components_model_luminous Switch Button (LED,12x12x7.3 mm) by Krizash on Thingiverse: https://www.thingiverse.com/thing:4484393

Summary:
Real luminous Switch Button  in Fusion 360 for your projects

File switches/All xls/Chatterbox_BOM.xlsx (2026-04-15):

Device: | Chatterbox
Version: | V1.0.0
Last Updated: | 2025-09-26
 |  |  |  |  |  |  |  | Total filament (g) |  | Unit Cost | Total Estimated Cost | Build Cost
 |  |  |  |  |  |  |  | 435 |  | $135.54 | $166.42
ID | Commercial Parts |  |  |  |  |  |  |  |  | $109.87 | $108.74
 | Part | Description | Model | Manufacturer | Supplier | QTY / Device | QTY / PKG | PKGs | $/ PKG | $ / Device | Total Estimated Cost |  | Link
 | Micro Controller (Seeeduino Nano) |  |  | Seeed Technology, Ltd. | Digikey | 1 | 1 | 1 | $11.07 | $11.07 | $11.07 |  | https://www.digikey.ca/en/products/detail/seeed-technology-co-ltd/102010268/10290292
 | Audio Amplifier (Pam8302) |  |  | Adafruit Industries LLC | Digikey | 1 | 1 | 1 | $6.13 | $6.13 |  |  | https://www.digikey.ca/en/products/detail/adafruit-industries-llc/2130/5761279
 | Mono Speaker (4Ω 3W ) |  |  | Adafruit Industries LLC | Digikey | 1 | 1 | 1 | $6.13 | $6.13 |  |  | https://www.digikey.ca/en/products/detail/adafruit-industries-llc/2130/5761279
 | Audio Potentiometer |  |  | Same Sky (Formerly CUI Devices) | Digikey | 1 | 1 | 1 | $2.65 | $2.65 |  |  | https://www.digikey.ca/en/products/detail/cui-devices/PTN16-A10125K1A2/20380750
 | Micro SD Reader |  |  | Adafruit Industries LLC | Digikey | 1 | 1 | 1 | $10.93 | $10.93 |  |  | https://www.digikey.ca/en/products/detail/adafruit-industries-llc/254/5761230
 | Micro SD Card |  |  | Adafruit Industries LLC | Digikey | 1 | 1 | 1 | $7.69 | $7.69 |  |  | https://www.digikey.ca/en/products/detail/adafruit-industries-llc/5252/15841478
 | Microphone (MAX9814) |  |  | Adafruit Industries LLC | Digikey | 1 | 1 | 1 | $12.35 | $12.35 |  |  | https://www.digikey.ca/en/products/detail/adafruit-industries-llc/1713/4990777
 | Buttons (B3F-5050) |  |  | Omron Electronics Inc-EMC Div | Digikey | 4 | 1 | 4 | $0.57 | $2.28 |  |  | https://www.digikey.ca/en/products/detail/omron-electronics-inc-emc-div/B3F-5050/368377
 | Slide switch (SPST) |  |  | C&K | Digikey | 2 | 1 | 2 | $0.95 | $1.90 |  |  | https://www.digikey.ca/en/products/detail/c-k/os102011ma1qs1/1981431
 | 3.5 mm Mono Jack |  |  | Same Sky (Formerly CUI Devices) | Digikey | 2 | 1 | 2 | $2.17 | $4.34 |  |  | https://www.digikey.ca/en/products/detail/cui-devices/SJ1-3535NG/738699
 | Blue LED |  |  | Wurth Elektronik | Digikey | 4 | 1 | 4 | $0.37 | $1.48 |  |  | https://www.digikey.ca/en/products/detail/w%C3%BCrth-elektronik/151051BS04000/4490009
 | Resistor (2.2k Ω) |  |  | Stackpole Electronics Inc | Digikey | 12 | 1 | 12 | $0.16 | $1.92 |  |  | https://www.digikey.ca/en/products/detail/stackpole-electronics-inc/CF18JT2K20/1741619
 | 5 pin female header |  |  | Sullins Connector Solutions | Digikey | 2 | 1 | 2 | $0.55 | $1.10 |  |  | https://www.digikey.ca/en/products/detail/sullins-connector-solutions/PPTC051LFBN-RC/807239
 | 15 pin female header |  |  | Sullins Connector Solutions | Digikey | 2 | 1 | 2 | $1.19 | $2.38 |  |  | https://www.digikey.ca/en/products/detail/sullins-connector-solutions/PPTC151LFBN-RC/810153
 | Battery, 9V |  |  | Duracell Industrial Corporation, Inc. | Digikey | 1 | 1 | 1 | $7.49 | $7.49 |  |  | https://www.digikey.ca/en/products/detail/duracell-industrial-operations-inc/9V/21259959
 | Capacitor, 10 uF |  | FG24X7R1A106KRT06 | TDK Corporation | Digikey | 3 | 1 | 3 | $0.50 | $1.50 |  |  | https://www.digikey.ca/en/products/detail/tdk-corporation/FG24X7R1A106KRT06/5802984
 | 9V Battery Clip |  |  | Keystone Electronics | Digikey | 1 | 1 | 1 | $0.86 | $0.86 |  |  | https://www.digikey.ca/en/products/detail/keystone-electronics/232/303804
 | #4 Sheet Metal Screw | #4 x 3/8" pan head, Phillips drive |  | Serpac | Digikey | 20 | 1 | 20 | $0.61 | $12.20 |  |  | https://www.digikey.ca/en/products/detail/serpac/6005/307599
 | Ribbon Cable |  |  | Assmann WSW Components | Digikey | 1 | 1 | 1 | $1.63 | $1.63 |  |  | https://www.digikey.ca/en/products/detail/assmann-wsw-components/H3DDS-1006G/1218627
 | Ribbon Cable Header |  |  | Amphenol ICC (FCI) | Digikey | 2 | 1 | 2 | $0.79 | $1.58 |  |  | https://www.digikey.ca/en/products/detail/amphenol-cs-fci/86130101014345E1LF/7592367
 | Slide switch (SPDT) |  |  | C&K | Digikey | 2 | 1 | 2 | $1.21 | $2.42 |  |  | https://www.digikey.ca/en/products/detail/c-k/os103011ma7qp1/1981432
 | 24 gauge wire | May be useful to buy two colours |  | TE Connectivity Raychem Cable Protection | Digikey | 9 | 10 | 1 | $10.11 | $9.10 |  |  | https://www.digikey.ca/en/products/detail/te-connectivity-raychem-cable-protection/55A0111-24-9/2399803
 | 8 pin female header |  |  | Sullins Connector Solutions | Digikey | 1 | 1 | 1 | $0.74 | $0.74 |  |  | https://www.digikey.ca/en/products/detail/sullins-connector-solutions/PPTC081LFBN-RC/810147
 | Custom PCB |  |  |  |  |  |  |  |  | $8.00 | $40.00
 | Part | Description |  | Manufacturer | Supplier | QTY / Device | QTY / PKG | PKGs | $/ PKG | $ / Device | Total Estimated Cost |  | Link
 | Main PCB | Main PCB board |  |  |  | 1 | 5 | 1 | $5.00 | $1.00 | $5.00
 | Secondary PCB | Secondary PCB board |  |  |  | 1 | 5 | 1 | $5.00 | $1.00 | $5.00
 | LED PCB | Boards for LEDs |  |  |  | 4 | 20 | 1 | $5.00 | $1.00 | $5.00
 |  | Shipping |  |  |  | 1 | 5 | 1 | $25.00 | $5.00 | $25.00
 | 3D Printed Parts |  |  |  |  |  |  | 707 |  | $17.68 | $17.68
 | Part | Description | Filament Type | Filament | Color | QTY / Device | Mass (g) / Part | Total Mass | $ / kg | $ / Device | Total Estimated Cost |  | Link
 | Enclosure Bottom - Left |  | PLA |  | Any | 1 | 106 | 106 | $25.00 | $2.65 | $2.65 |  | 2h49m
 | Enclosure Bottom - Right |  | PLA |  | Any | 1 | 109 | 109 | $25.00 | $2.73 | $2.73 |  | 2h32m
 | Enclosure Top - Left |  | PLA |  | Any | 1 | 89 | 89 | $25.00 | $2.23 | $2.23 |  | 2h17m
 | Enclosure Top - Right |  | PLA |  | Any | 1 | 86 | 86 | $25.00 | $2.15 | $2.15 |  | 2h17m
 | Label Holder |  | PLA |  | Any | 4 | 19 | 76 | $25.00 | $1.90 | $1.90 |  | 31m (each)
 | Button Base |  | PLA |  | Any | 4 | 26 | 104 | $25.00 | $2.60 | $2.60 |  | 41m (each)
 | Button Cap |  | PLA |  | Any | 4 | 13 | 52 | $25.00 | $1.30 | $1.30 |  | 27m (each)
 | Button Insert |  | PLA |  | Any | 4 | 7 | 28 | $25.00 | $0.70 | $0.70 |  | 22m (each)
 | Centre Support |  | PLA |  | Any | 2 | 24 | 48 | $25.00 | $1.20 | $1.20 |  | 49m (each)
 | Volume Knob |  | PLA |  | Any | 1 | 2 | 2 | $25.00 | $0.05 | $0.05 |  | 13m
 | Battery Cover |  | PLA |  | Any | 1 | 7 | 7 | $25.00 | $0.18 | $0.18 |  | 20m
 | Tools
 | Tool | Description |  | Manufacturer | Supplier |  |  |  |  |  |  |  | Link
 | Soldering Iron
 | 60Pb/40Tn Solder Wire
 | Needle Nose Pliers
 | Flush Cutters
 | Wire strippers
 | Desolder Pump (Optional)
 | Alternatives
 | Part | Description |  | Manufacturer | Supplier | QTY / Device | QTY / PKG | PKGs | $/ PKG | $ / Device | Total Estimated Cost |  | Link

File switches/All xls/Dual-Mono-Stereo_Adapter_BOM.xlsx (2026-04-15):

Device: Dual Mono-Stereo Adapter |  | Total Cost | Total Print time (hr) | Total filament (g)
Version: V1.0 | Date Created: 4/20/2021 | $5.98 | 0.63 | 6.37
Commercial Parts
Part type (Electrical, Mechanical, Sanitization, etc) | Part Name | Qty Needed | Pkg Qty | $ / pkg | $/unit | Price for qty needed | Link
Electrical | Stereo Jack | 3 | 1 | $1.94 | $1.94 | $5.82 | https://www.digikey.ca/product-detail/en/cui-inc/SJ1-3535NG/CP1-3535NG-ND/738699
 |  |  |  |  |  |  | https://www.amazon.ca/gp/product/B01M1PAL43/ref=ppx_yo_dt_b_search_asin_title?ie=UTF8&psc=1
3D Printed Parts ESTIMATED PRICING USING 1KG ROLL COST: | $25.00
Part | Description | Quantity Needed | TOTAL Mass (g) | Estimated Price | Print Time (Min) | Link
Top Enclosure |  | 1 | 3.84 | $0.10 | 22
Bottom Enclosure |  | 1 | 2.53 | $0.06 | 16
 |  |  |  | $0.00
 |  |  |  | $0.00
 |  |  |  | $0.00
 |  |  | Total Print Cost: | $0.16
Tools for Assembly
Alternatives (if there are other sources for some parts link them below)
Part and description | Link

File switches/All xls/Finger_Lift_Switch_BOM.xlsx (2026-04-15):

Finger Lift Switch for SunnyHill |  |  |  |  |  | $10.37 | $65.62
Part | Description | QTY | QTY/PKG | Min PKGs | Cost/PKG | Unit Cost | Total Cost | Source
Bearing, MR85-2RS, ID: 5 mm, OD: 8 mm, Thickness: 2.5 mm | Bearing | 1 | 10 | 1 | $14.14 | $1.41 | $14.14 | https://www.amazon.ca/MR85-2RS-Groove-Bearings-Double-Sealed/dp/B08JKG5D39
Reed Switch, 2 mm x 14 mm, Normally Open (N/O) | Reed Switch | 1 | 20 | 1 | $11.99 | $0.60 | $11.99 | https://www.amazon.ca/ARTGEAR-Contact-Normally-Magnetic-Induction/dp/B07V2YB2L3
M3 Screw & Nut Kit | M3 Screw & Nut Kit | 1 | 10 | 1 | $11.99 | $1.20 | $11.99 | https://www.amazon.ca/340pcs-Phillips-Stainless-Assortment-Thread/dp/B075RCVVYN?s=hi
Magnet, Neodymium, 5x1mm | Magnet | 2 | 200 | 1 | $13.99 | $0.14 | $13.99 | https://www.amazon.ca/Multi-Use-Refrigerators-Magnets-Whiteboard-Bulletin/dp/B07JDBLVBZ
Nut, 1/4 - 20 medium strength steel hex nut, zinc plated | Mounting Nut | 1 | 1 | 1 | $0.12 | $0.12 | $0.12 | https://www.homedepot.ca/product/paulin-1-4-20-inch-finished-hex-nut-zinc-plated-grade-5-unc-50pcs/1000123233
Cable, M/M, 3.5 mm mono, 10 ft | Mono cable | 1 | 2 | 1 | $12.99 | $6.50 | $12.99 | https://www.amazon.ca/TNP-3-5mm-Mono-Cable-10FT/dp/B01M3NBUD1
Filament, PLA, 1.7 mm, 3850 mm | filament @ $34.99/Kg Density 1.24g/cm3 No Markups | 1 | 1 | 1 | $0.40 | $0.40 | $0.40 | https://www.ic3dprinters.com/3d-printer-job-cost-calculator/#_calc-anchor

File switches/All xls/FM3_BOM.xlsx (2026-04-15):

Reference | Quantity | Description | Footprint | Digikey | Farnell | Mouser | RS Components | other vendor | Orientation critical
FLipMouse Mainboard
A1 | 1 | ABX00052 - Arduino Nano RP2040 Connect | FLipMouse:NANO_33_Footprint_SMD_Castell_AlignmentHoles | 1050-ABX00052-ND | 3769782 | 782-ABX00052 | 222-1485 |  | yes
BZ1 | 1 | PKMCS0909E4000 | Buzzer_Beeper:Buzzer_Murata_PKMCS0909E | 490-9647-1-ND | 2529461 | 81-PKMCS0909E4000-R1 | 901-0898 |  | no
C1, C5, C6 | 3 | 100n | Capacitor_SMD:C_0603_1608Metric | 1276-CL10B104KB8NNNLCT-ND | 3013409 | 581-06035C104K4 | 200-6519 |  | no
C2 | 1 | 1n | Capacitor_SMD:C_0603_1608Metric | 1276-1018-1-ND | 9406174 | 80-C0603C102K8RAUTO | 133-5657 |  | no
C3 | 1 | 100uF/6.3V | Capacitor_SMD:C_1210_3225Metric | 1276-1092-1-ND | 3778295 | 187-CL32A107MQVNNNE | 766-1166 |  | no
D1, D2, D3, D4 | 4 | SFH4045 | FLipMouse:SFH4045N | 475-3047-1-ND | 2981752 | 720-SFH4045N | 876-8729 |  | yes
D5, D6 | 2 | 5mm WS2812B | LED_THT:LED_D5.0mm-4_RGB_Wide_Pins | 1528-1959-ND | -- | -- | -- | Adafruit 1938 | yes
D8, D9 | 2 | PESD5V0S1BA,115 | Diode_SMD:D_SOD-323 | 1727-3837-1-ND | 8737690 | 771-PESD5V0S1BA-T/R | 508-737 |  | yes
J2 | 1 | SSM-104-L-SV | Connector_PinSocket_2.54mm:PinSocket_1x04_P2.54mm_Vertical_SMD_Pin1Right | S5596-ND | 2847903 | 200-SSM104LSV | 765-5385 |  | yes
J3, J4 | 2 | FC68125 | FLipMouse:FC68125 | 3185-FC68125-ND | 2309468 | -- | 805-1655 |  | yes
J5 | 1 | Wuerth 690367280676 | FLipMouse:690367280676 | 732-1965-1-ND | 1641849 | 710-690367280676 | 771-8109 |  | yes
Q2 | 1 | BSS806 | Package_TO_SOT_SMD:SOT-23 | BSS806NH6327XTSA1CT-ND | 2443469 | 726-BSS806NH6327XT | 827-0109 (250pcs!) |  | yes
R1 | 1 | 4k7 | Resistor_SMD:R_0603_1608Metric | 1292-WR06X472JTLCT-ND | 3994558 | 756-WCR0603-4K7FI | 199-5594 |  | no
SW1 | 1 | SKHHLQA010 | Button_Switch_THT:SW_Tactile_SPST_Angled_PTS645Vx58-2LFS | -- | 2056827 | 688-SKHHLQ | 758-1991 |  | yes
SW2 | 1 | EVQP7C01P | Button_Switch_SMD:SW_SPST_EVQP7C | P16765CT-ND | 2860917 | 667-EVQP7C01P | 238-3732 |  | yes
U2 | 1 | MPRLS0025PA00001A | FLipMouse:Honeywell-MPRLS0025PA00001AB-0 | MPRLS0025PA00001A | 2811406 | 785-MPRLS0025PA00001 | 197-6897 |  | yes
U4 | 1 | TSOP4838 | OptoDevice:Vishay_MOLD-3Pin | TSOP4838-ND | 4913190 | 782-TSOP4838 | 708-5115 (or 90pcs: 919-0014) |  | yes
-- | 1 | PCB | Source: https://github.com/asterics/FLipMouse/raw/master/Hardware/PCB-design/mainboard/FM3_mainboard.kicad_pcb |  |  |  |  | Aisler.net
FLipMouse Sensorboard
C1, C6 | 2 | 1uF | Capacitor_SMD:C_0603_1608Metric | 1276-6524-1-ND | 3013384 | 581-06036C105MAT2A | 184-3898 |  | no
C2, C3, C4, C5, C7 | 5 | 100nF | Capacitor_SMD:C_0603_1608Metric | 1276-CL10B104KB8NNNLCT-ND | 3013409 | 581-06035C104K4 | 200-6519 |  | no
J1 | 1 | Wuerth 690367280676 | Project:690367280676 | 732-1965-1-ND | 1641849 | 710-690367280676 | 771-8109 |  | yes
J2, J4, J5, J6 | 4 | BF350-3AA | Project:straingauges |  |  |  |  | Amazon/Aliexpress | yes
R1, R2 | 2 | 4k7 | Resistor_SMD:R_0603_1608Metric | 1292-WR06X472JTLCT-ND | 3994558 | 756-WCR0603-4K7FI | 199-5594 |  | no
R3, R4, R5, R6 | 4 | 47R | Resistor_SMD:R_0603_1608Metric | P47.0HCT-ND | 2447378 | 603-RC0603JR-1347RL | 199-5584 |  | no
RN1 | 1 | CAY16-1001F4LF | Resistor_SMD:R_Array_Convex_4x0603 | CAY16-1001F4LFCT-ND | 1770141 | 652-CAY16-1001F4LF | 181-4454 |  | no
U1 | 1 | NAU7802-SGI | Package_SO:SOP-16_3.9x9.9mm_P1.27mm | NAU7802SGI-ND | -- | -- | -- |  | yes
-- | 1 | PCB | Source: https://github.com/asterics/FLipMouse/raw/master/Hardware/PCB-design/sensorboard/RES-DMS-NAU7802.kicad_pcb |  |  |  |  | Aisler.net
FLipMouse 3D printed parts
base | 1 | case base, printed in PETG grey or orange | Source: https://github.com/asterics/FLipMouse/blob/master/Hardware/case-design/FM3_case-base.stl
lid | 1 | case lid, printed in PETG grey or orange | Source: https://github.com/asterics/FLipMouse/blob/master/Hardware/case-design/FM3_case-lid.stl
front | 1 | case front, printed in GreenTec white | Source: https://github.com/asterics/FLipMouse/blob/master/Hardware/case-design/FM3_case-front_white.stl
-- | 4 | M2 nuts | Must be printed in the white front part (pause the print @3.2mm height) | -- | 1419445 | -- | 560-271 | hardware store | PRINTED WITHIN FRONT
washer/spacer | 2 | plastic washers, printed in GreenTec | Source: https://github.com/asterics/FLipMouse/blob/master/Hardware/case-design/FM3_LuerSpacer.stl
FLipMouse mechanical / others
 | 1 | Hot shoe adapter (mounting) | Search for 3/8“ hotshoe adapter on Ali/Banggood/… |  |  |  |  | Amazon: B00RSXM3U2
 | 1 | Female LuerLock | must have a M5 thread. |  |  |  |  | Droh.de: VBM-CHLLFB20
 | 1 | Silicone tube 2x4mm (ID/OD); 45mm length | Local hardware store or equal |  |  |  |  | Persicaner: ESSI02X04
 | 1 | PE/PVC tube 4x6mm (ID/OD); 5mm length | Local hardware store or equal |  |  |  |  | Persicaner: PLTU04X06
 | 1 | 6pin IDC flat ribbon cable, 1.27mm raster, 70mm, 28AWG |  | 3M157967-100-ND | 2064503 | 517-3365/06-100 | 815-8003
 | 2 | Würth IDC crimp connector 690157000672 |  | 732-1989-5-ND | 1641882 | 710-690157000672 | 121-6765
 | 2 | M2x16mm | Would recommend Philips head; Local hardware store or equal | -- |  | -- | 179-5689 | Conrad.at
 | 4 | M2x10mm | Would recommend Philips head; Local hardware store or equal | 2266-FM-210-0025P-ND |  | -- | 908-7646 | Conrad.at
FLipMouse mouthpiece
 | 1 | Male LuerLock | must have a M6 thread. |  |  |  |  | Droh.de: VBM-CHLLM06
 | 1 | Acryllic pipe, 6x10mm (ID/OD); 50/100/120/150mm length |  |  |  |  |  | Acrylhaus.com: 100629-001
FLipMouse packaging / accessory
 | 1 | USB cable, USB Micro connector | Please use a magnetic connector to save the USB plug on the Arduino. Works best with a 90° connector.
 | 1 | Packaging (device) | Ratioform 167-5W |  |  |  |  | Ratioform.at
 | 1 | Packaging (parcel) | Ratioform W129 |  |  |  |  | Ratioform.at

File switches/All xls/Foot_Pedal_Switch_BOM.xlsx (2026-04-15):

Foot Pedal Switch |  | Total Cost | Total Print time (hr) | Total filament (g)
Version: V1.2 | Last updated: 2024-Sept-16 | $14.84 | 1.73 | 17
Commercial Parts:
Part type (Electrical. Mechanical, Sanitization, ect) | Part Name | Quantity Needed | Pkg Quantity | Price per package | Price per Unit | Price for qty needed | Link
Electrical | Stereo Terminal Block | 1 | 1 | $3.60 | $3.60 | $3.60 | https://www.digikey.ca/en/products/detail/adafruit-industries-llc/2790/7241423
Electrical | Foot Switch | 1 | 1 | $10.81 | $10.81 | $10.81 | https://www.digikey.ca/en/products/detail/adafruit-industries-llc/423/5353597
3D Printed Parts ESTIMATED PRICING USING 1KG ROLL COST: | $25.00
Part | Description | Quantity Needed | TOTAL Mass (g) | Estimated Price | Print Time (Min) | Link
Bracket V2 | bracket to mount foot pedal to the ground | 1 | 17 | $0.43 | 104
 |  |  |  | $0.00
 |  |  |  | $0.00
 |  |  |  | $0.00
 |  |  |  | $0.00
 |  |  | Total Print Cost: | $0.43
Tools for Assembly
Wire stripper
Screwdriver
Alternatives (if there are other sources for some parts link them below)
Part and description | Link | Price
Metal Foot Pedal alternative (2-pack) | amazon.ca/gp/product/B09WN6MVVH | $23.85

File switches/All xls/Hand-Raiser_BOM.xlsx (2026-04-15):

Device: Hand-Raiser |  | Total Cost | Total Print time (hr) | Total filament (g)
Version: V1.0 | Date Created: MAY 2022 | $12.15 | 1.17 | 10
Commercial Parts:
Part type (Electrical. Mechanical, Sanitization, ect) | Part Name | Quantity Needed | Pkg Quantity | Price per package | Price per Unit | Price for qty needed | Link
Microcontroller Board | Adafruit Trinket M0 | 1 | 1 | $8.95 | $8.95 | $8.95 | Adafruit Trinket M0 - for use with CircuitPython & Arduino IDE : ID 3500 : $8.95 : Adafruit Industries, Unique & fun DIY electronics and kits (https://www.adafruit.com/product/3500)
USB Cable | USB A to Micro-B | 1 | 1 | $2.95 | $2.95 | $2.95 | USB cable - USB A to Micro-B [3 foot long] : ID 592 : $2.95 : Adafruit Industries, Unique & fun DIY electronics and kits (https://www.adafruit.com/product/592)
3D Printed Parts ESTIMATED PRICING USING 1KG ROLL COST: | $25.00
Part | Description | Quantity Needed | TOTAL Mass (g) | Estimated Price | Print Time (Min) | Link
Snap Back | Piece that the micro controller snaps onto | 1 | 3 | $0.07 | 13
Snap Hanger | Piece used to hang the device | 1 | 3 | $0.07 | 21
Face Plate | Clear piece that covers LED light | 1 | 4 | $0.10 | 36
 |  |  | Total Print Cost: | $0.25
Tools for Assembly
Computer with Windows
Alternatives (if there are other sources for some parts link them below)
Part and description | Link

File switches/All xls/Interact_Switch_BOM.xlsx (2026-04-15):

Device: | Interact Switch
Version: | V2.0
Last Updated: | 2025-07-08
 |  |  |  |  |  |  |  | Total filament (g) |  | Unit Cost | Total Estimated Cost | Build Cost
 |  |  |  |  |  |  |  | 35 |  | $8.70 | $8.70
ID | Commercial Parts |  |  |  |  |  |  |  |  | $7.82 | $7.82
 | Part | Description |  | Manufacturer | Supplier | QTY / Device | QTY / PKG | PKGs | $/ PKG | $ / Device | Total Estimated Cost |  | Link
 | Mono Cable |  |  |  | Digikey | 1 | 1 | 1 | $4.65 | $4.65 | $4.65 |  | https://www.digikey.ca/en/products/detail/tensility-international-corp/10-00344/2350247
 | Snap Action Switch |  |  |  | Digikey | 1 | 1 | 1 | $1.40 | $1.40 | $1.40 |  | https://www.digikey.ca/en/products/detail/omron-electronics-inc-emc-div/SS-3GP/664724
 | #4 Sheet Metal Screw |  |  |  | Digikey | 3 | 1 | 3 | $0.59 | $1.77 | $1.77 |  | https://www.digikey.ca/en/products/detail/serpac/6005/307599
 |  |  |  |  |  |  |  | 0 |  | $0.00 | $0.00
 |  |  |  |  |  |  |  | 0 |  | $0.00 | $0.00
 | 3D Printed Parts |  |  |  |  |  |  | 35 |  | $0.88 | $0.88
 | Part | Description | Filament Type | Filament | Color | QTY / Device | Mass (g) / Part | Total Mass | $ / kg | $ / Device | Total Estimated Cost |  | Link
 | Interact_Switch_Base |  | PLA |  | Any | 1 | 17 | 17 | $25.00 | $0.43 | $0.43
 | Interact_Switch_Cap_Plain |  | PLA |  | Any | 1 | 14 | 14 | $25.00 | $0.35 | $0.35
 | Interact_Switch_Holder |  | PLA |  | Any | 1 | 3 | 3 | $25.00 | $0.08 | $0.08
 | Interact_Switch_Insert_0.6mm |  | PLA |  | Any | 1 | 1 | 1 | $25.00 | $0.03 | $0.03
 |  |  |  |  |  |  |  | 0 |  | $0.00 | $0.00
 |  |  |  |  |  |  |  | 0 |  | $0.00 | $0.00
 |  |  |  |  |  |  |  | 0 |  | $0.00 | $0.00
 |  |  |  |  |  |  |  | 0 |  | $0.00 | $0.00

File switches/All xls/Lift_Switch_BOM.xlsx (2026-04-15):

 | Lift Switch |  |  |  |  |  |  |  | Total filament (g) |  |  | Unit Cost | Total Cost | Total Print time (hr)
 | Version: | 2.0 |  | Last updated: | 2024-Mar-25 |  |  |  | 15 |  |  | $42.99 | $77.57 | 1:51:00
ID | Part | Description |  | Manufacturer | MPN | Supplier | Supplier PN | QTY | QTY / PKG | PKGs | $/PKG | Price per Unit | Total Price |  | Link | Alternate
 | Electronics
C | XA2 | PRO TRINKET LI-BATTERY BACKPACK |  | Adafruit Industries LLC | 2124 | Digi-Key | 1528-1443-ND | 1 | 1 | 1 | 7.29 | $7.29 | $7.29 |  | https://www.digikey.ca/en/products/detail/adafruit-industries-llc/2124/5761211
B | XA1 | TRINKET M0 ATSAMD21E18 EVAL BRD |  | Adafruit Industries LLC | 3500 | Digi-Key | 1528-2361-ND | 1 | 1 | 1 | 13.17 | $13.17 | $13.17 |  | https://www.digikey.ca/en/products/detail/adafruit-industries-llc/3500/7623049
D | J1 | CONN JACK STEREO 3.5MM TH R/A |  | Kycon, Inc. | STX-3000 | Digi-Key | 2092-STX-3000-ND | 1 | 1 | 1 | 1.18 | $1.18 | $1.18 |  | https://www.digikey.ca/en/products/detail/kycon-inc/STX-3000/9975995
H | SW1 | SWITCH SLIDE SPDT 100MA 12V |  | Nidec Copal Electronics | CSS-1210TB | Digi-Key | 563-1091-1-ND | 1 | 1 | 1 | 0.91 | $0.91 | $0.91 |  | https://www.digikey.ca/en/products/detail/nidec-components-corporation/CSS-1210TB/1124209
E | U1 | DIP-4 400V/120 MA, SSR RELAY SPS |  | Bright Toward Industrial Co., Ltd. | AB30 | Digi-Key | 3008-AB30-ND | 1 | 1 | 1 | 2.72 | $2.72 | $2.72 |  | https://www.digikey.ca/en/products/detail/bright-toward-industrial-co-ltd/AB30/13556959
G | SW2 | 6 X 7.4 MM, 15.3 MM ACTUATOR HEI |  | CUI Devices | TS11-674-153-BK-260-RA-D | Digi-Key | 2223-TS11-674-153-BK-260-RA-D-ND | 1 | 1 | 1 | 0.24 | $0.24 | $0.24 |  | https://www.digikey.ca/en/products/detail/cui-devices/TS11-674-153-BK-260-RA-D/16562823
F | R1 | RES 330 OHM 5% 1/4W AXIAL |  | YAGEO | CFR-25JB-52-330R | Digi-Key | 330QBK-ND | 1 | 1 | 1 | 0.16 | $0.16 | $0.16 |  | https://www.digikey.ca/en/products/detail/yageo/CFR-25JB-52-330R/1636
I |  | 3.5 mm digital output plug |  | CUI Devices | SP-3533-02 | Digi-Key | 102-4747-ND | 1 | 1 | 1 | 2.68 | $2.68 | $2.68 |  | https://www.digikey.ca/en/products/detail/cui-devices/SP-3533-02/9486641
M |  | LIGHT PIPE RA. 150 3MM ROUND |  | Bivar Inc | SLP3-150-450-R | Digikey | 492-2519-ND | 1 | 1 | 1 | 1.19 | $1.19 | $1.19 |  | https://www.digikey.ca/en/products/detail/bivar-inc/SLP3-150-450-R/4926816
N |  | 3.7V 110 mAh lithium-ion polymer battery |  | Canada Robotix | 0930 | Canada Robotix |  | 1 | 1 | 1 | 5.99 | $5.99 | $5.99 |  | https://www.canadarobotix.com/products/939
Q |  | M2x0.4 x 25 mm screws, flat head |  | McMaster Carr | 92010A111 | McMaster Carr | 92010A111 | 3 | 50 | 1 | $9.31 | $0.56 | $9.31 |  | https://www.mcmaster.com/catalog/130/3484/92010A111
 |  |  |  |  |  |  |  |  |  | 0 |  | $0.00 | $0.00
 | Custom PCB
 | Part | Description |  | Manufacturer |  | Supplier | Supplier PN | QTY | QTY / PKG | PKG | $/PKG | Price per Unit | Total Price |  | Link
A | PCB1 | Lift Switch Adapter Custom PCB |  | JLCPCB |  |  |  | 1 | 5 | 1 | 7.28 | 1.46 | 7.28
 | PCB Shipping | PCB Shipping - DHL Express | Shipping |  |  |  |  | 1 | 5 | 1 | 25 | 5 | 25
 | PCB Shipping | PCB Shipping - Fedex International | Shipping |  |  |  |  | 0 | 5 | 0 | 25 | 0 | 0
 | 3D Printed Parts ESTIMATED PRICING USING 1KG ROLL COST: | $30.00
 | Part | Description |  |  |  |  |  | QTY | Mass (g) |  | Estimated Price | Estimated Price | Estimated Price | Print Time (hr:Min) | Link
O.1 |  | Lift Switch Base |  |  |  |  |  | 1 | 6 |  | $0.18 | $0.18 | $0.18 | 0:41:00
O.2 |  | Lift Switch Top |  |  |  |  |  | 1 | 8 |  | $0.24 | $0.24 | $0.24 | 1:07:00
P |  | Lift Switch Power Switch |  |  |  |  |  | 1 | 1 |  | $0.03 | $0.03 | $0.03 | 0:03:00
 |  |  |  |  |  |  |  |  |  |  | $0.00 | $0.00 | $0.00
 | Alternatives
 | Part | Description |  | Manufacturer |  | Supplier
 |  |  |  |  |  |  |  |  | 1 | 0 |  | $0.00 | $0.00
 |  |  |  |  |  |  |  |  | 1 | 1 |  | $0.00 | $0.00
 |  |  |  |  |  |  |  |  | 1 | 1 |  | $0.00 | $0.00

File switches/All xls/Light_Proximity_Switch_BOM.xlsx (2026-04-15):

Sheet: Electronics
Qty | Component | Component name | Supplier | Manufacturer | MPN | Digi-Key Part Number | Unit Cost (CAD) | Build Cost (CAD) | Link
1 | IC1 | IC OPAMP GP 1 CIRCUIT 8DIP | DigiKey | Microchip Technology | MCP6231-E/P | MCP6231-E/P-ND | $0.69 | $0.69 | https://www.digikey.ca/en/products/detail/microchip-technology/MCP6231-E-P/716239?s=N4IgTCBcDaILIGEAKA2MBmAjAWgKIHolsA5AERAF0BfIA
2 | D1,D3 | SENSOR PHOTODIODE 850NM 2DIP | DigiKey | OSRAM | BPW34 | 475-1070-ND | $1.63 | $3.26 | https://www.digikey.ca/product-detail/en/osram-opto-semiconductors-inc/BPW34/475-1070-ND/607274
1 | D2 | Schottky diode 1N5817 | DigiKey | STMicroelectronics | 1N5817 | 497-4547-1-ND | $0.33 | $0.33 | https://www.digikey.ca/en/products/detail/stmicroelectronics/1N5817/770963
1 | LED1 | LED GREEN CLEAR 5MM ROUND | DigiKey | Cree LED | C566D-GFF-CY14Q7S1 | C566D-GFF-CY14Q7S1-ND | $0.43 | $0.43 | https://www.digikey.ca/en/products/detail/cree-led/C566D-GFF-CY14Q7S1/4793750
1 | C1 | CAP CER 10000PF 50V Z5U RADIAL | DigiKey | KEMET | C315C103M5U5TA7301 | 399-13973-1-ND | $0.40 | $0.40 | https://www.digikey.ca/product-detail/en/kemet/C315C103M5U5TA7301/399-13973-1-ND/6562544
2 | C2,C5 | CAP CER 33PF 50V X7R RADIAL | DigiKey | KEMET | C315C330K2G5TA7301 | 399-13940-1-ND | $0.54 | $1.08 | https://www.digikey.ca/product-detail/en/kemet/C315C330K2G5TA7301/399-13940-1-ND/6562533
1 | C3 | CAP CER 10PF 50V C0G/NP0 RADIAL | DigiKey | Vishay Siliconix | K100J15C0GF5TL2 | BC1001CT-ND | $0.35 | $0.35 | https://www.digikey.ca/product-detail/en/vishay-bc-components/K100J15C0GF5TL2/BC1001CT-ND/286623
1 | C4 | CAP CER 1UF 25V X7R RADIAL | DigiKey | KEMET | C315C105K3R5TA | 399-9714-ND | $1.32 | $1.32 | https://www.digikey.ca/en/products/detail/kemet/C315C105K3R5TA/3726118
1 | R1 | TRIMMER 100K OHM 0.5W PC PIN TOP | DigiKey | Bourns Inc. | 3386P-1-104TLF | 3386P-104TLF-ND | $3.39 | $3.39 | https://www.digikey.ca/product-detail/en/bourns-inc/3386P-1-104TLF/3386P-104TLF-ND/1232548
1 | R3 | 200K Resistor | DigiKey | Yageo | CFR-25JB-52-200K | 200KQBK-ND | $0.15 | $0.15 | https://www.digikey.ca/product-detail/en/yageo/CFR-25JB-52-200K/200KQBK-ND/711
1 | R2 | RES 10K OHM 1/4W 5% AXIAL | DigiKey | Yageo | CFR-25JB-52-10K | 10KQBK-ND | $0.15 | $0.15 | https://www.digikey.ca/product-detail/en/yageo/CFR-25JB-52-10K/10KQBK-ND/338
1 | B1 | CR2032 battery holder | DigiKey | Memory Protection Devices | BU2032SM-BT-GTR | BU2032SM-FH-GCT-ND | $1.88 | $1.88 | https://www.digikey.ca/en/products/detail/mpd-memory-protection-devices/BU2032SM-BT-GTR/2439521
1 | S1 | SWITCH SLIDE SPDT 200MA 30V | DigiKey | E-Switch | EG1218 | EG1903-ND | $1.21 | $1.21 | https://www.digikey.ca/product-detail/en/e-switch/EG1218/EG1903-ND/101726
1 | 3.5mm Cable | CBL ASSY 3.5MM SLIM 6' MONO BLK | DigiKey | Tensility International Corp | 10-00344 | 839-1039-ND | $3.49 | $3.49 | https://www.digikey.ca/product-detail/en/tensility-international-corp/10-00344/839-1039-ND/2350247
1 | Cable Tie | Cable Tie, Nylon, 71 mm long, 1.8 mm wide | Digikey | Panduit | PLT.6SM-C | PLT.6SM-C | $0.32 | $0.32 | https://www.digikey.ca/en/products/detail/panduit-corp/PLT-6SM-C/280029
2 | Screws | M2X8mm screw | DigiKey | APM Hexseal | RM2X8MM 2701 | 335-1155-ND | $1.14 | $2.28 | https://www.digikey.ca/product-detail/en/apm-hexseal/RM2X8MM-2701/335-1155-ND/612919
2 | Q1,Q2 | MOSFET N-CH 100V 1A 4-DIP | Amazon |  | IRLD110PBF |  | $1.28 | $2.55 | https://www.amazon.ca/10PCS-IRLD110-DIP4-IRLD110PBF-DIP-4/dp/B0DSSJTPH8
1 | CR2032 | CR2032 3V Battery | Amazon | AmazonBasics | CR2032 |  | $0.73 | $0.73 | https://www.amazon.ca/AmazonBasics-Lithium-CR2032-Batteries-10-Pack/dp/B07RXJ4S7Z
 |  |  |  |  |  | Total Electronics Cost | $24.01 | $24.01

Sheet: PCB
Qty | Manufacturer | Fabrication Time | Delivery option | Delivery Cost (USD) | Fabrication Cost(USD) | Tax (USD) | Total Cost (USD) | Total Cost (CAD) | Unit Cost (CAD) | Link
5 | JLCPCB | 1-2 days for green and 3-4 for other colors | *S.F Express( 3-5 business days) | $24.82 | $2 | $15.00 | $41.82 | $55.62 | $11.12 | https://jlcpcb.com
5 | JLCPCB | 1-2 days for green and 3-4 for other colors | *DHL Express ( 3-5 business days) | $20.22 | $2 | $15.00 | $37.22 | $49.50 | $9.90 | https://jlcpcb.com
5 | JLCPCB | 1-2 days for green and 3-4 for other colors | Registered Air Mail (15-20 business days) | $9.47 | $2 | $0.00 | $11.47 | $15.26 | $3.05 | https://jlcpcb.com
10 | JLCPCB | 3-4 days for green and 5-6 for other colors | *S.F Express( 3-5 business days) | $24.82 | $5 | $15.00 | $44.82 | $59.61 | $5.96 | https://jlcpcb.com
10 | JLCPCB | 3-4 days for green and 5-6 for other colors | *DHL Express ( 3-5 business days) | $20.22 | $5 | $15.00 | $40.22 | $53.49 | $5.35 | https://jlcpcb.com
10 | JLCPCB | 3-4 days for green and 5-6 for other colors | Registered Air Mail (15-20 business days) | $9.47 | $5 | $0.00 | $14.47 | $19.25 | $1.92 | https://jlcpcb.com
50 | JLCPCB | 5-6 days for green | *S.F Express( 3-5 business days) | $24.82 | $12.80 | $15.00 | $52.62 | $69.98 | $1.40 | https://jlcpcb.com
50 | JLCPCB | 7-8 for other colors | *S.F Express( 3-5 business days) | $24.82 | $27.30 | $15.00 | $67.12 | $89.27 | $1.79 | https://jlcpcb.com
50 | JLCPCB | 5-6 days for green | *DHL Express ( 3-5 business days) | $20.22 | $12.80 | $15.00 | $48.02 | $63.87 | $1.28 | https://jlcpcb.com
50 | JLCPCB | 7-8 for other colors | *DHL Express ( 3-5 business days) | $20.22 | $27.30 | $15.00 | $62.52 | $83.15 | $1.66 | https://jlcpcb.com
50 | JLCPCB | 5-6 days for green | Registered Air Mail (15-20 business days) | $13.29 | $12.80 | $0.00 | $26.09 | $34.70 | $0.69 | https://jlcpcb.com
50 | JLCPCB | 7-8 for other colors | Registered Air Mail (15-20 business days) | $13.29 | $27.30 | $0.00 | $40.59 | $53.98 | $1.08 | https://jlcpcb.com
5 | PCBWay | 1-2 days for green and 3-4 for other colors | *DHL Express ( 3-5 business days) | $21 | $5 | $15.00 | $41.00 | $54.53 | $10.91 | https://www.pcbway.com/
5 | PCBWay | 1-2 days for green and 3-4 for other colors | China Post ( 10-15 business days) | $7 | $5 | $0.00 | $12.00 | $15.96 | $3.19 | https://www.pcbway.com/
5 | PCBWay | 1-2 days for green and 3-4 for other colors | E-packet ( 25-40 business days) | $6 | $5 | $0.00 | $11.00 | $14.63 | $2.93 | https://www.pcbway.com/
5 | PCBWay | 1-2 days for green and 3-4 for other colors | *FedEx IE (6-10 business days) | $26 | $5 | $15.00 | $46.00 | $61.18 | $12.24 | https://www.pcbway.com/
10 | PCBWay | 1-2 days for green and 3-4 for other colors | *DHL Express ( 3-5 business days) | $21 | $5 | $15.00 | $41.00 | $54.53 | $5.45 | https://www.pcbway.com/
10 | PCBWay | 1-2 days for green and 3-4 for other colors | E-packet ( 10-15 business days) | $7 | $5 | $0.00 | $12.00 | $15.96 | $1.60 | https://www.pcbway.com/
10 | PCBWay | 1-2 days for green and 3-4 for other colors | China Post ( 25-40 business days) | $7 | $5 | $0.00 | $12.00 | $15.96 | $1.60 | https://www.pcbway.com/
10 | PCBWay | 1-2 days for green and 3-4 for other colors | *FedEx IE (6-10 business days) | $26 | $5 | $15.00 | $46.00 | $61.18 | $6.12 | https://www.pcbway.com/
50 | PCBWay | 1-2 days for green and 3-4 for other colors | *DHL Express ( 3-5 business days) | $28 | $27 | $15.00 | $70.00 | $93.10 | $1.86 | https://www.pcbway.com/
50 | PCBWay | 1-2 days for green and 3-4 for other colors | E-packet ( 10-15 business days) | $11 | $27 | $0.00 | $38.00 | $50.54 | $1.01 | https://www.pcbway.com/
50 | PCBWay | 1-2 days for green and 3-4 for other colors | China Post ( 25-40 business days) | $11 | $27 | $0.00 | $38.00 | $50.54 | $1.01 | https://www.pcbway.com/
50 | PCBWay | 1-2 days for green and 3-4 for other colors | *FedEx IE (6-10 business days) | $26 | $27 | $15.00 | $68.00 | $90.44 | $1.81 | https://www.pcbway.com/
5 | SeeedStudio Fusion | 3-4 for all colors (2 more days for Matte Black ) | *DHL ( 1-3 business days) | $23.8 | $4.9 | $15.00 | $43.70 | $58.12 | $11.62 | https://www.seeedstudio.com
5 | SeeedStudio Fusion | 3-4 for all colors (2 more days for Matte Black ) | *FedEx (4-8 business days) | $24.55 | $4.9 | $15.00 | $44.45 | $59.12 | $11.82 | https://www.seeedstudio.com
10 | SeeedStudio Fusion | 3-4 for all colors (2 more days for Matte Black ) | *DHL ( 1-3 business days) | $23.8 | $4.9 | $15.00 | $43.70 | $58.12 | $5.81 | https://www.seeedstudio.com
10 | SeeedStudio Fusion | 3-4 for all colors (2 more days for Matte Black ) | *FedEx (4-8 business days) | $24.55 | $4.9 | $15.00 | $44.45 | $59.12 | $5.91 | https://www.seeedstudio.com
50 | SeeedStudio Fusion | 3-4 for all colors (2 more days for Matte Black ) | *DHL ( 1-3 business days) | $26.70 | $26.36 | $15.00 | $68.06 | $90.52 | $1.81 | https://www.seeedstudio.com
50 | SeeedStudio Fusion | 3-4 for all colors (2 more days for Matte Black ) | *FedEx (4-8 business days) | $28.54 | $26.36 | $15.00 | $69.90 | $92.97 | $1.86 | https://www.seeedstudio.com
100 | SeeedStudio Fusion | 3-4 for all colors (2 more days for Matte Black ) | *DHL ( 1-3 business days) | $29.60 | $39.13 | $15.00 | $83.73 | $111.36 | $1.11 | https://www.seeedstudio.com
100 | SeeedStudio Fusion | 3-4 for all colors (2 more days for Matte Black ) | *FedEx (4-8 business days) | $32.50 | $39.13 | $15.00 | $86.63 | $115.22 | $1.15 | https://www.seeedstudio.com
3 | OSH Park | Prototype (9-12 business days) [1] |  |  | $15.85 |  |  |  |  | https://oshpark.com/
6 | OSH Park | Prototype (9-12 business days) [1] |  |  | $31.7 |  |  |  |  | https://oshpark.com/
9 | OSH Park | Prototype (9-12 business days) [1] |  |  | $47.55 |  |  |  |  | https://oshpark.com/
12 | OSH Park | Prototype (9-12 business days) [1] |  |  | $63.40 |  |  |  |  | https://oshpark.com/
21 | OSH Park | Prototype (9-12 business days) [1] |  |  | $110.95 |  |  |  |  | https://oshpark.com/
51 | OSH Park | Prototype (9-12 business days) [1] |  |  | $269.45 |  |  |  |  | https://oshpark.com/
102 | OSH Park | Prototype (9-12 business days) [1] |  |  | $538.90 |  |  |  |  | https://oshpark.com/
3 | OSH Park | Super Swift (4-5 business days) [2] |  |  | $31.70 |  |  |  |  | https://oshpark.com/
6 | OSH Park | Super Swift (4-5 business days) [2] |  |  | $63.40 |  |  |  |  | https://oshpark.com/
9 | OSH Park | Super Swift (4-5 business days) [2] |  |  | $95.1 |  |  |  |  | https://oshpark.com/
12 | OSH Park | Super Swift (4-5 business days) [2] |  |  | $126.80 |  |  |  |  | https://oshpark.com/
21 | OSH Park | Super Swift (4-5 business days) [2] |  |  | $221.90 |  |  |  |  | https://oshpark.com/
51 | OSH Park | Super Swift (4-5 business days) [2] |  |  | $538.90 |  |  |  |  | https://oshpark.com/
102 | OSH Park | Super Swift (4-5 business days) [2] |  |  | $1077.80 |  |  |  |  | https://oshpark.com/
40 | OSH Park | Bulk Order (9-14 business days) [3] |  |  | $126.80 |  |  |  |  | https://oshpark.com/
50 | OSH Park | Bulk Order (9-14 business days) [3] |  |  | $158.50 |  |  |  |  | https://oshpark.com/
100 | OSH Park | Bulk Order (9-14 business days) [3] | Standard First Class Mail(5-21 business days) | $0 | $317 | $0 | $317.00 | $421.61 | $4.22 | https://oshpark.com/
100 | OSH Park | Bulk Order (9-14 business days) [3] | UPS Saver (1 business day) | $33 | $317 | $15.00 | $365.00 | $485.45 | $4.85
 | 1 | $5 per square inch, which includes three copies of your design
 | 2 | $10 per square inch, which includes three copies of your design
 | 3 | $1 per square inch, 100 square inch minimum.

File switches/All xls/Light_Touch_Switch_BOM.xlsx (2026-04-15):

Device: | Light Touch Switch
Version: | V1.0.0
Last Updated: | 2024-06-26
 |  |  |  |  |  |  |  | Total filament (g) |  | Unit Cost | Total Estimated Cost | Build Cost
 |  |  |  |  |  |  |  | 8 |  | $5.89 | $5.89
Maker Guide ID | Commercial Parts |  |  |  |  |  |  |  |  | $5.69 | $5.69
 | Part | Description |  | Manufacturer | Supplier | QTY / Device | QTY / PKG | PKGs | $/ PKG | $ / Device | Total Estimated Cost |  | Link
A01 | Tactile switch | Tactile switch for controlling devices |  | Omron | Digikey | 1 | 1 | 1 | $1.02 | $1.02 | $1.02 |  | https://www.digikey.ca/en/products/detail/omron-electronics-inc-emc-div/B3F-5050/368377?s=N4IgTCBcDaIEIGYBiBaArABkyAugXyA
A02 | 3.5 mm mono cable (6 foot length) | Cable to connect to an assistive device |  | Tensility International Corp | Digikey | 1 | 1 | 1 | $4.67 | $4.67 | $4.67 |  | https://www.digikey.ca/en/products/detail/tensility-international-corp/10-00344/2350247
 |  |  |  |  |  |  |  | 0 |  | $0.00 | $0.00
 |  |  |  |  |  |  |  | 0 |  | $0.00 | $0.00
 |  |  |  |  |  |  |  | 0 |  | $0.00 | $0.00
 | 3D Printed Parts |  |  |  |  |  |  | 12 |  | $0.20 | $0.20
 | Part | Description | Filament Type | Filament | Color | QTY / Device | Mass (g) / Part | Total Mass | $ / kg | $ / Device | Total Estimated Cost |  | Link
A03 | LTS_Base_v1.0.stl | Switch base | PLA |  | Any | 1 | 3 | 3 | $25.00 | $0.08 | $0.08
A04 | LTS_Cap_v1.0.stl | Switch top | PLA |  | Any | 1 | 4 | 4 | $25.00 | $0.10 | $0.10
A05 | LTS_Pin_v0.1.stl | Pins for holding base and top together | PLA |  | Any | 1 | 1 | 1 | $25.00 | $0.03 | $0.03
T06 | Switch_Jig_12mm_V1.0.stl | Optional 3D printed jig to hold tactile switch while soldering | PLA |  | Any | 1 | 4 | 4
 | Tools
 | Tool | Description |  | Manufacturer | Supplier |  |  |  |  |  |  |  | Link
T01 | Wire cutter / stripper
T02 | Flush cutter
T03 | Soldering iron
T04 | Hot glue gun
T05 | Needle Nosed Pliers
T07 | Switch Testing Device
 | Alternatives
 | Part | Description |  | Manufacturer | Supplier | QTY / Device | QTY / PKG | PKGs | $/ PKG | $ / Device | Total Estimated Cost |  | Link
A01 | Tactile switch | Tactile switch for controlling devices |  | Omron | Mouser | 1 | 1 | 1 | $0.83 | $0.83 | $0.83 |  | https://www.mouser.ca/ProductDetail/Omron-Electronics/B3F-5050?qs=dOLq8QE0Pqqk%2FO9x2OpTQw%3D%3D
A02 | 3.5mm mono cable (six foot length) | Cable to connect to assistive devices |  | My Cable Mart | My Cable Mart | 0.5 | 1 | 1 | $1.77 | $0.89 | $1.77 |  | https://www.mycablemart.com/store/cart.php?m=product_detail&p=5537
A02 | 3.5mm mono cable (six foot length) | Cable to connect to assistive devices |  | Prime Cables | Prime Cable | 0.5 | 1 | 1 | 2.29 | 1.145 | 2.29 |  | https://www.primecables.ca/p-370665-cab-aud-200-all-35mm-18-inch-mono-ts-male-to-male-28awg-ft4-cable-black?from_pla=google&sku=383505&gad_source=1
A02 | 3.5 mm stereo cable (6 foot length) | Cable to connect to assistive devices. Note: You will need to do extra work to ensure the tip, ring, and sleeve are connected properly. |  | Prime Cables | Prime Cables | 0.5 | 1 | 1 | $1.99 | $0.99 | $1.99 |  | https://www.primecables.ca/p-391548-cab-aud-220-06-6ft-35mm-stereo-male-to-male-cable-riser-rated-cl2ft4-black?from_pla=google&sku=417835&gad_source=1

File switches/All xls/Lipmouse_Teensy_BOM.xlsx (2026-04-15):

Device | Package | Parts | Description | Qty | Farnell.com | Digikey.com | RS-Components | aliexpress.com | Others | Pin count | critical mounting Position/direction | Price Single | Price 100 Pieces | all prices excl. VAT (€ if not otherwise noted)
FLIpmouse – electronic parts
31-XX | B3F-31XX | S1 | TE – SPST-NO, short button | 1 | 2452343 | 450-1656-ND | 718-2370 |  |  | 4 | yes | 0.086 | 0.078
31-XX | B3F-31XX | S2 | EVQPF108K SWITCH, long Button | 1 | 2079506 | P10884S-ND | 756-1599 |  |  | 4 | yes | 0.18 | 0.13
FE05-1 | FE05-1 | SV1 | MALE HEADER, 90°, 1x5 | 1 | 2356179 | 732-5338-ND | 828-1667 |  |  | 5 | yes | 0.37 | 0.208
LED3MM | LED3MM | LED1 | LED red – MCL514PD | 1 | 1581128 | 160-1708-ND |  |  |  | 2 | yes | 0.153 | 0.0689
LED3MM | LED3MM | LED2 | LED yellow – MCL514YD | 1 | 1581131 | 160-1946-ND |  |  |  | 2 | yes | 0.249 | 0.0848
LED3MM | LED3MM | LED3 | LED green – MCL514GD | 1 | 1581130 | 160-1710-ND |  |  |  | 2 | yes | 0.198 | 0.0848
MA05-2 | MA05-2 | AUX | MALE HEADER, 2x5; Harwin M20 | 1 | 1022236 | 952-2124-ND |  |  |  | 10 | - | 0.258 | 0.222
RN04 | RN-5 | RN1 | Resistor network, 220R | 1 | 2333623 | 4605X-101-221LF-ND |  |  |  | 5 | yes | 0.362 | 0.153
RN04 | RN-5 | RN2 | Resistor network, 10k | 1 | 9356061 | 4605X-101-103LF-ND |  |  |  | 5 | yes | 0.381 | 0.208
MPXV7007GP | SMP_MX3V7007 | U$2 | 5V pressure sensor | 1 |  | MPXV7007GP-ND |  |  | AVNet.com: MPXV7007GP (9,13€) | 8 | yes | 13.95 | 9.3
TeensyLC – pin header | MA14-1 | -- | MALE HEADER, 1x14 | 2 | 2356164 | 732-5325-ND |  |  | Alternative: 2356174 (farnell) / 732-5333-ND (digikey) For all 3 pin headers | 14 | - | 1.77 | 0.896
TeensyLC – pin header | MA05-1 | -- | MALE HEADER, 1x5 | 1 | 2356157 | 732-5318-ND |  |  |  | 5 | - | 0 | 0
MA02-1 | MA02-1 | I2C | MALE HEADER, 1x2 | 1 | 2356153 | 732-5315-ND |  |  |  | 2 | - | 0 | 0
C-EU025-025X050 | C025-025X050 | C1,C2 | 100nF capacitor | 2 | 2112751 | 478-4855-ND |  |  |  | 2 | - | 0.21 | 0.121
1503_02 | 1503_02 | X1,X2 | Jack plugs JISC 6560 | 2 | 1216979 |  |  |  |  | 4 | yes | 2.82 | 2.28
24LC256P | 24LC256P | IC1 | I2C EEPROM | 1 | 9757970 | 24LC256-I/P-ND | 454-371 |  |  | 8 | yes | 0.84 | 0.681
R-EU_0309/V | 0309V | R1,R2,R3,R11 | 4k7, blue, | 4 | 9343253 |  |  |  |  | 2 | - | 0.174 | 0.0765
LED5MM | LED5MM | LED5 | LED | 1 | 3152856 | 751-1204-ND | 699-7635 (or 50pcs: 818-7663) |  |  | 2 | yes | 0.122 | 0.104
R-EU_0309/V | 0309V | R12 | 12R, min 0.25W | 1 | 9338420 | CFR-50JB-52-12R |  |  |  | 2 | - | 0.061 | 0.04
Piezo buzzer | EFBAA40D101 | SG1 | piezo buzzer | 1 | 1300026 |  | 457-011 |  | Cheaper at rs-components | 2 | - | 0.61 | 0.51
TSOP4838 | TSOP2XXX | U3 | TSOP4838 | 1 | 4913190 | TSOP4838-ND | 708-5115 (or 90pcs: 919-0014) |  |  | 3 | yes | 1.06 | 0.539
BS170 | TO-92 | Q1 | N-MOS FET, BS170 | 1 | 2453831 | BS170_D75ZCT-ND | 671-4736 |  |  | 3 | yes | 0.138 | 0.138
FllipMouse daughterboard & mechanical parts
header 5pol | FE05-1 | SV1 | FEMALE HEADER, 1x5 | 1 |  | SAM1122-05-ND |  |  | Alternative: 9728910 (Farnell, for 7) | 5 | yes | 0.9028571429 | 0.75
FSR | -- | -- | FSR Sensor | 4 |  | 1027-1000-ND |  |  | Electrade.de: FSR400 | 2 | yes | 31.36 | 17.6
Daughterboard PCB | -- | -- | -- | 1 |  |  |  |  | PCBPool, etc. | - | yes | 8 | 0
Spacer – adjusting pin header/LEDs | -- | -- | -- | 1 |  |  |  |  | self printed | 5 | - | 0.35 | 0.2
M4 plate | -- | -- | -- | 4 | 7047496 |  |  |  |  | - | yes | 2.49 | 0.2075
LuerLock | -- | -- | -- | 1 |  |  |  | Search for „luer lock m5“ | www.droh.de: CHLLFB20 | - | - | 5 | 2.98
Plastic pipe 5cm, 4/2mm dia | -- | -- | -- | 1 |  |  |  |  | e.g. Amazon: B00K5U4TE8 | - | - | 1.7 | 0.085
Flipmouse Teensy, PCB | -- | -- | -- | 1 |  |  |  |  | PCBPool, etc. | - | - | 8 | 3.44
Compression spring (0.5x7x15mm) | -- | -- | -- | 4 |  |  |  |  | federnshop.com: D-068A-02 | - | - | 10.32 | 0.266
Rubber pads | -- | -- | -- | 4 | 1165074 | SJ5003-0-ND |  |  |  | - | yes | 4.88 | 0.3485714286
TEENSYLC | TEENSY_3.1_BASIC | TEENSYLC | TeensyLC | 1 |  | 1568-1233-ND |  |  | watterott.com (or: PJRC.com) | 33 | yes | 12.5 | 12.5
Mouthpiece | -- | -- | -- | 1 |  |  |  |  | https://quadjoy.com/shop/ | - | - | 7.5 | 6.5
Hot shoe adapter (mounting) | -- | -- | -- | 1 |  |  |  | Search for „3/8" hot shoe mount“ | Amazon: B00RSXM3U2 | - | - | 2.18 | 1.2
USB cable | -- | -- | -- | 1 | -- | -- |  | Search for „MicroUSB cable 1m“ |  | -- | -- | 2 | 2
USB stick | -- | -- | -- | 1 | -- | -- |  | Search for „8GB USB Stick orange“ |  | -- | -- | 4 | 3
Packaging | -- | -- | -- | 1 | -- | -- |  | -- | -- | -- | -- | 6 | 6
Parts ONLY for Lasercut – Acrylic case
M4x25 screw | -- | -- | -- | 4 | 7070706 | 36-29358-ND |  |  |  | - | yes | 0.92 | 0.2036
Glue | -- | -- | -- | 1 | -- | -- |  | -- |  | -- | -- | 4 | 4
Acrylic glass case set | -- | -- | -- | 1 |  |  |  |  | Lasercut | - | yes | 4 | 2
M3x06 screw | -- | -- | -- | 4 | 7070585 | 36-29341-ND |  |  |  | - | - | 5.68 | 0.2272
Parts ONLY for 3D printed case
M3x06 screw | -- | -- | -- | 2 | 7070585 | 36-29341-ND |  |  |  | - | - | 5.68 | 0.2272
M3x25 screw | -- | -- | -- | 4 |  |  |  |  |  | - | - | 0.92 | 0.2036
3D printed case | -- | -- | -- | 1 |  |  |  |  |  | - | - | 3 | 2
 |  |  |  |  |  |  |  |  |  |  | Sum (laser cut): | 145.77 | 79.43
 |  |  |  |  |  |  |  |  |  |  | Sum (3D print): | 140.77 | 75.43
 |  |  |  |  |  |  |  |  |  |  | Shipping costs: | 25.00 | 0.25
Packing material (box for kit) |  | Stülpkarton |  | 1 |  |  |  |  | Ratioform 167-5w |  |  | 1.69 | 1.39
Packing material (send carton) |  | Verpackungskarton |  | 1 |  |  |  |  | Ratioform W129 |  |  | 0.55 | 0.51
 |  |  |  |  |  |  |  |  |  |  | TOTAL (laser cut): | 207.62 | 97.90
 |  |  |  |  |  |  |  |  |  |  | TOTAL (3D print): | 201.62 | 93.10
 |  |  |  |  |  |  |  |  |  |  | Including 20% VAT

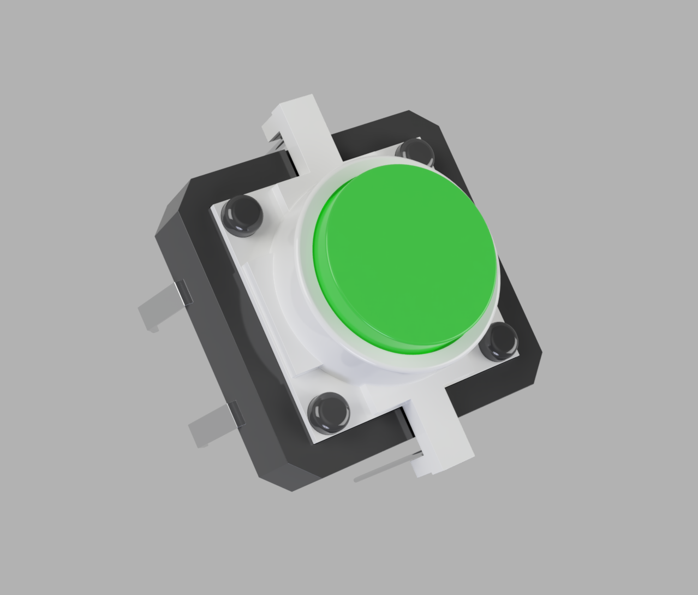
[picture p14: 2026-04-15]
TOSORT/components_model_luminous Switch Button (LED,12x12x7.3 mm) - 4484393/images/components_model_luminous_Switch_Button_LED12x12x7.3_mm_picture5.png

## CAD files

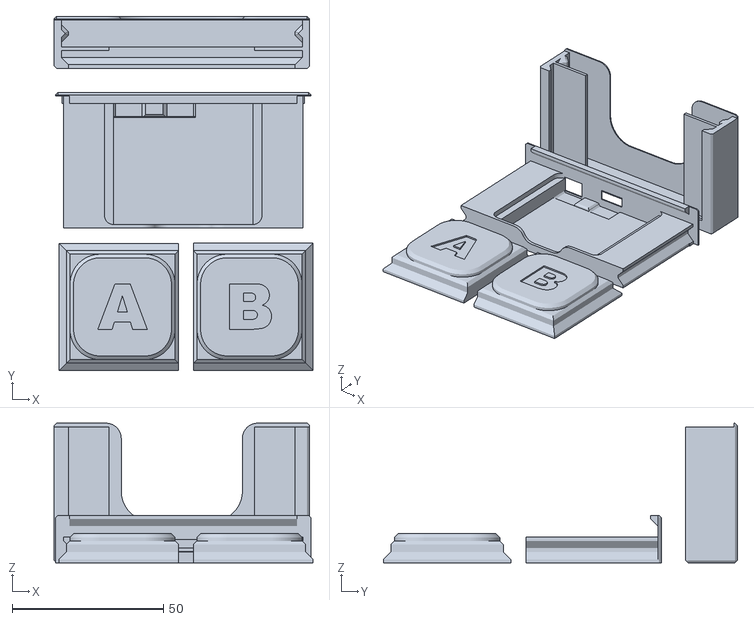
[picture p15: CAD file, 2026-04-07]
switches/PrintLab/TapPlus_+BluetoothDualSwitchAssistiveDevice/Main Set/full set.stl
85.5 x 116.9 x 46.1

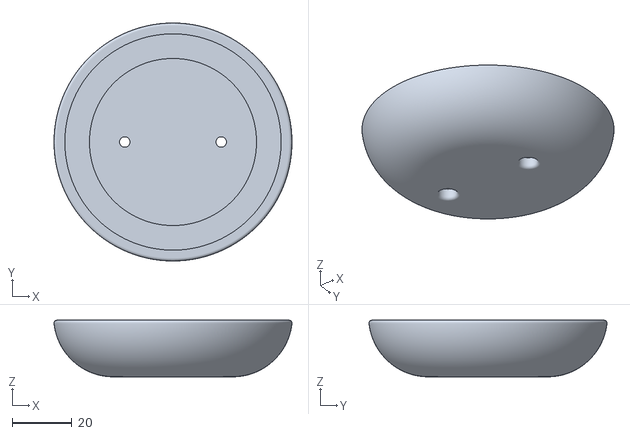
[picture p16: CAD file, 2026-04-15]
TOSORT/Adaptable switch _ ergonomic button - 3093824/files/ERGONOMIC_BUTTON_FULLCAP.stl
79.8 x 79.8 x 19.0

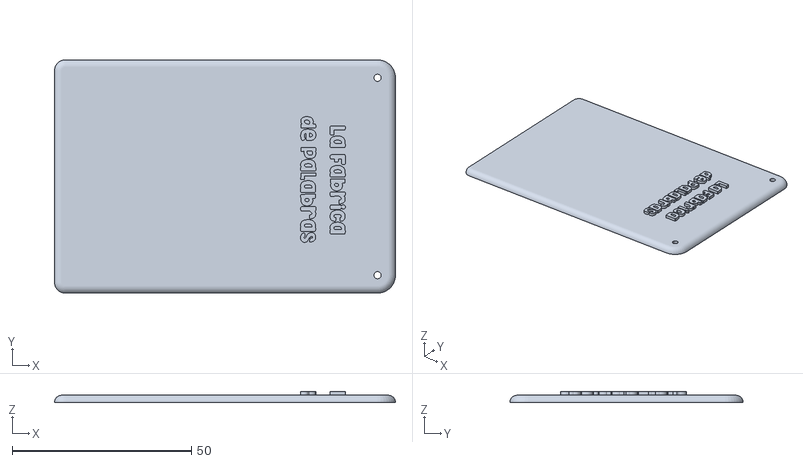
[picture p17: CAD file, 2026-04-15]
TOSORT/Botón, pulsador GRANDE_ big button - 3738291(1)/files/tapaensamblada.STL
95.0 x 65.0 x 3.00

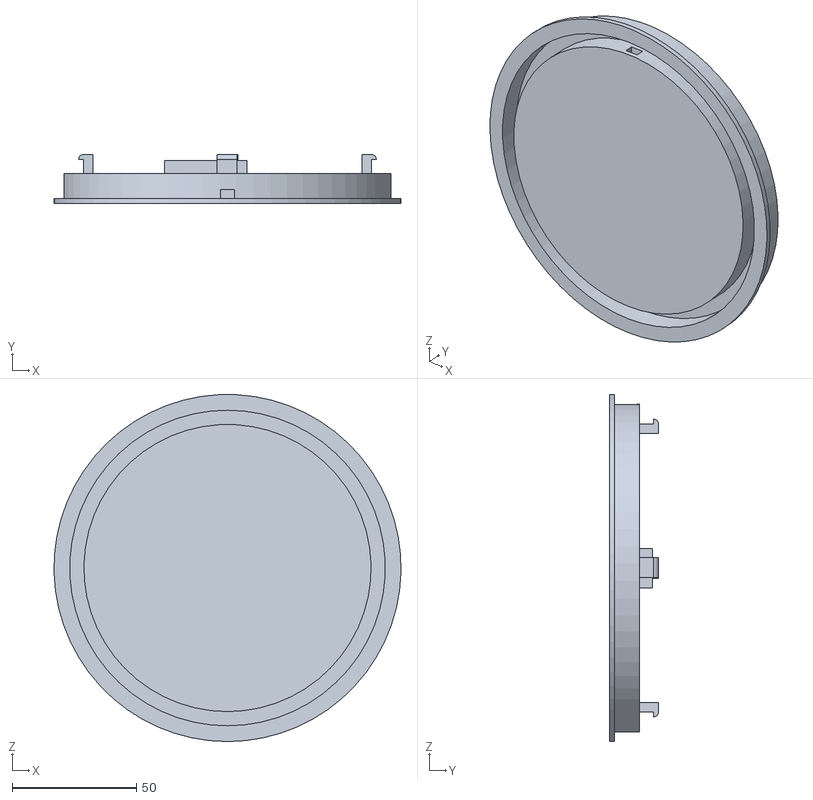
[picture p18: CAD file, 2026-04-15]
TOSORT/Large Surface Accessible Button - 6111368/files/BOTTOM_8_Full_with_Updated_Mount.STL
139.7 x 19.8 x 139.7

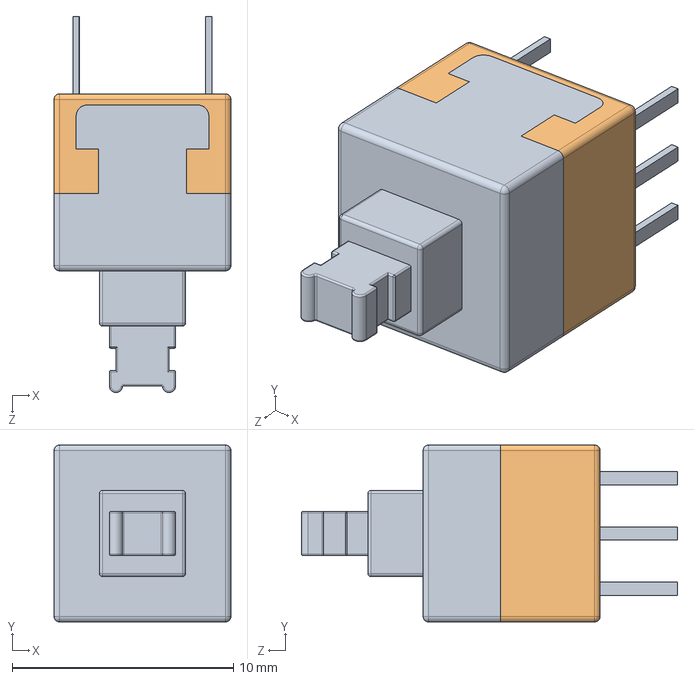
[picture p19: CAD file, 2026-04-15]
TOSORT/Push Button Switch - 704113/files/dpdt_pusch_button_switch_asm.SLDASM
8.00 x 8.00 x 17.0 mm
dpdt pusch button switch
dpdt pusch button switch part2

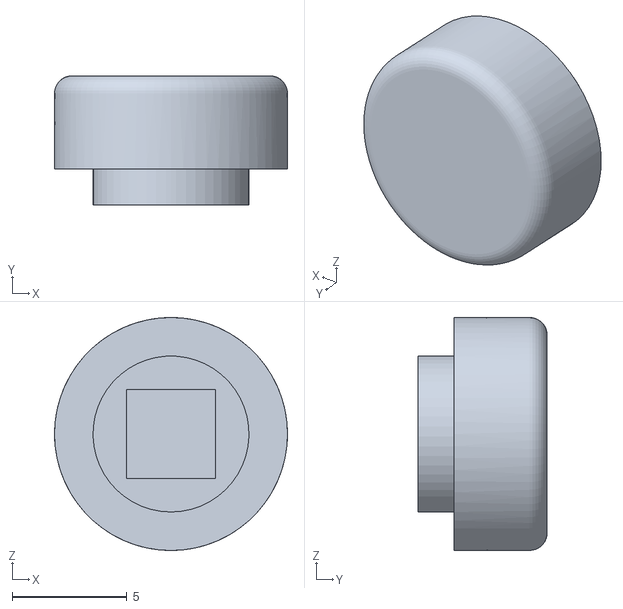
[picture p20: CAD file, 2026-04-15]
TOSORT/Single push button switch box - 2940716/files/ASSY_-_PUSH_BUTTON_CAP-1.STL
10.2 x 5.64 x 10.2

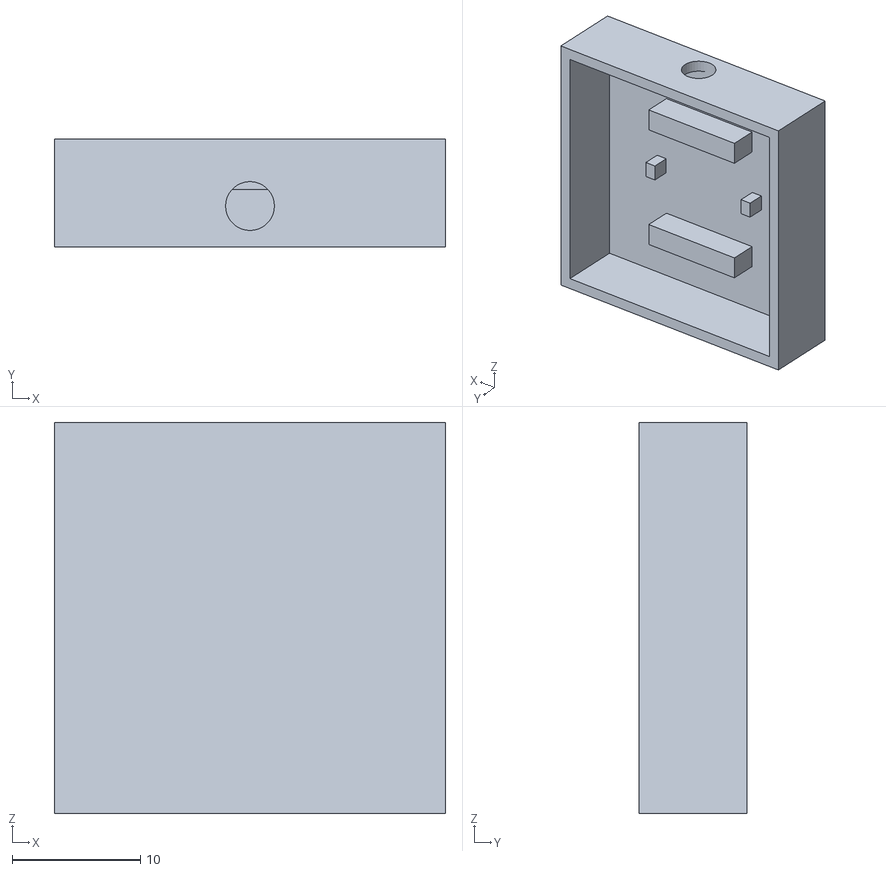
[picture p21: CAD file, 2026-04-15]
TOSORT/Single push button switch box - 2940716/files/ASSY_-_BACK_COVER-1.STL
30.5 x 8.38 x 30.5

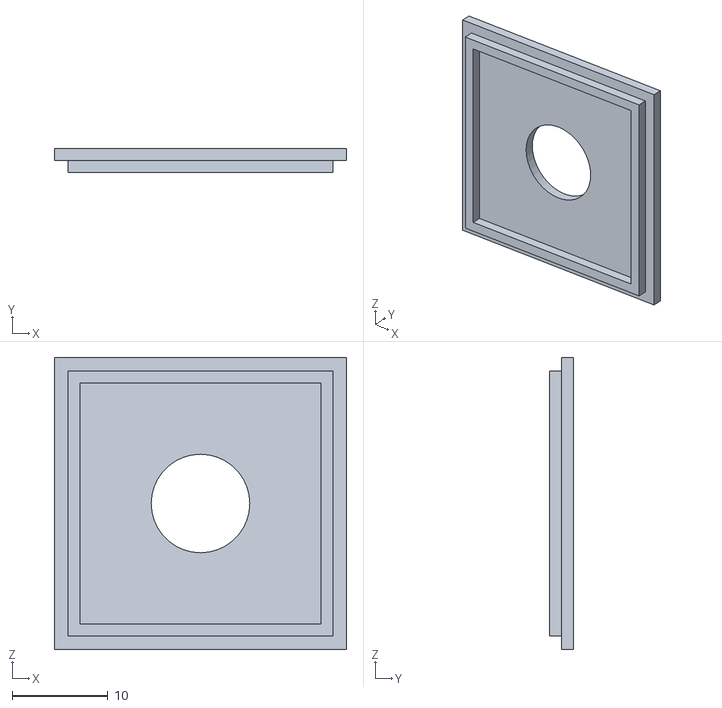
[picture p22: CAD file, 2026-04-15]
TOSORT/Single push button switch box - 2940716/files/ASSY_-_TOP_COVER-1.STL
30.5 x 2.54 x 30.5

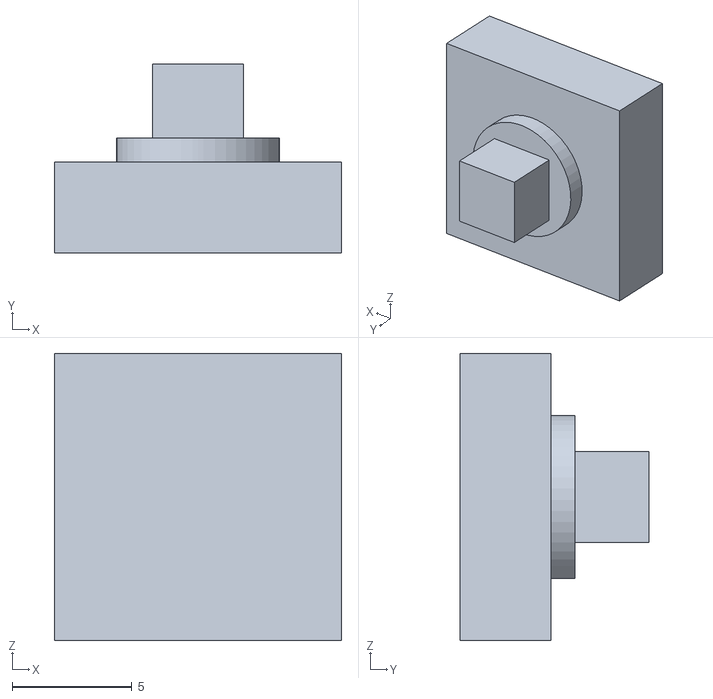
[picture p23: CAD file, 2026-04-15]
TOSORT/Single push button switch box - 2940716/files/ASSY_-_PUSH_BUTTON-1.STL
12.0 x 7.90 x 12.0

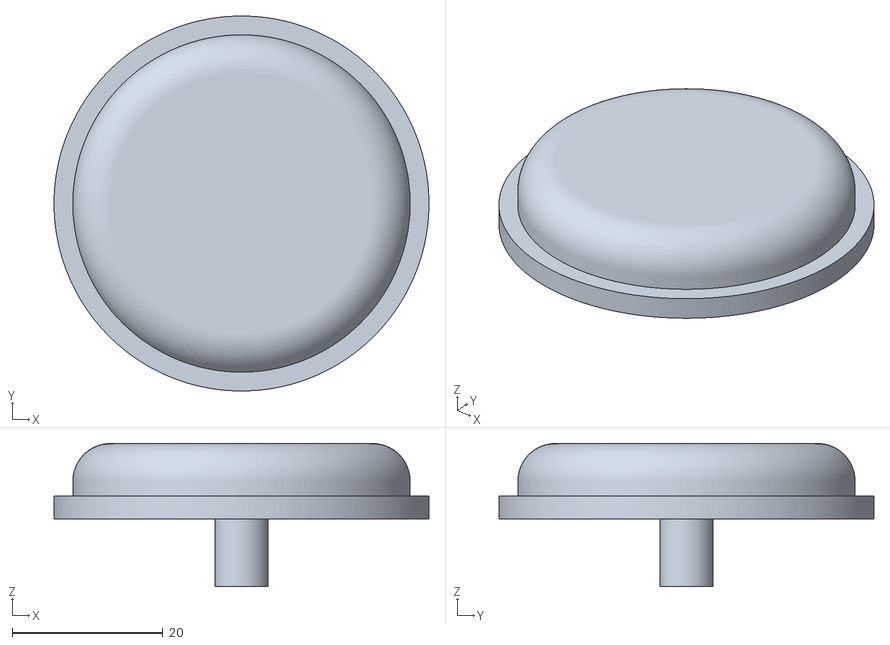
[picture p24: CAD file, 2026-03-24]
switches/atmakers/AT Switch Remix - 3583410/files/AT_Switch_Top.stl
49.8 x 49.8 x 19.0

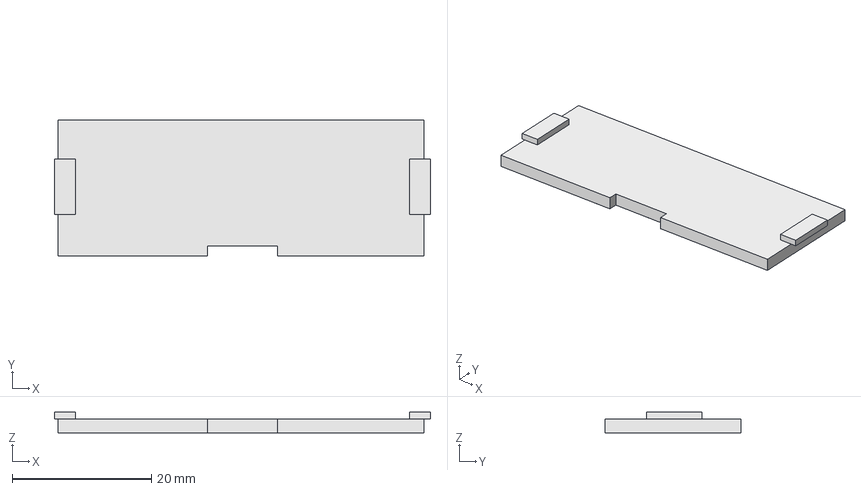
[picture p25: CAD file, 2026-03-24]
switches/misc/Adaptive_Assistive 3.5mm Button - 1471760/files/button_hatch.fcstd
54.0 x 19.6 x 3.00 mm

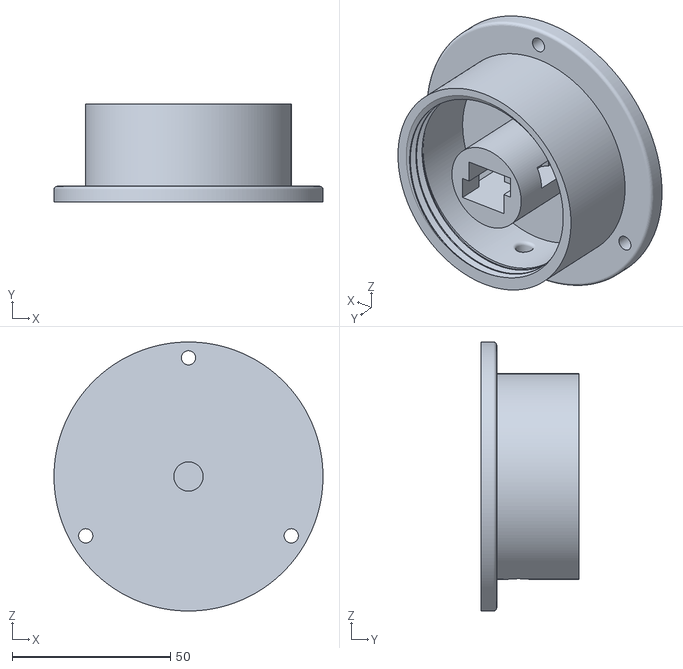
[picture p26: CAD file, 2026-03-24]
switches/misc/Modified AT Switch Design - 2507266/files/base.stl
85.0 x 31.0 x 85.0

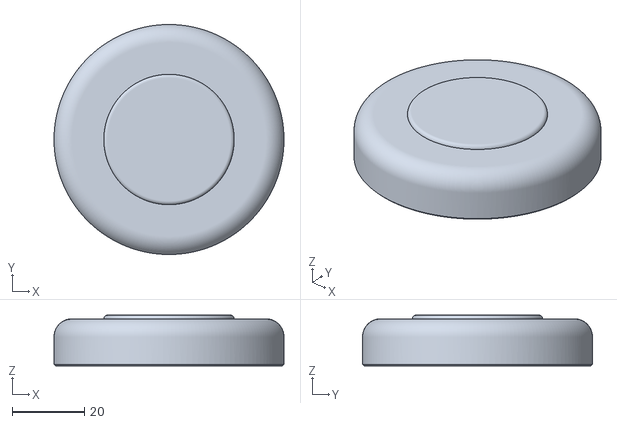
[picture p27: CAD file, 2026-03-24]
switches/mturvey/Interact SwitchCapPack/files/ButtonCap_Circle.STL
63.5 x 63.5 x 14.0

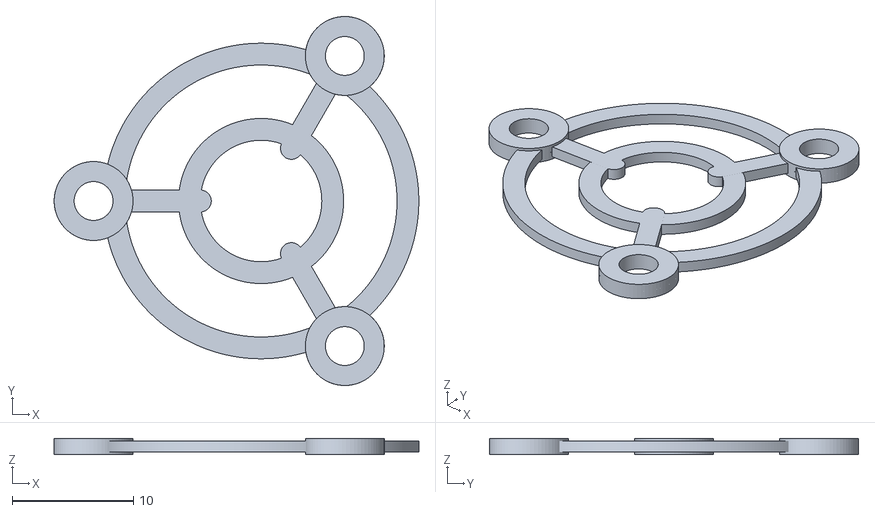
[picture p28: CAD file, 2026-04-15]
switches/Original_Designs/custom_Switch/stl/flexure_spring.stl
30.1 x 30.4 x 1.35

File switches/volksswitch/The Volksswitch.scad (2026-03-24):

// Written by Volksswitch <www.volksswitch.org>
//
// To the extent possible under law, the author(s) have dedicated all
// copyright and related and neighboring rights to this software to the
// public domain worldwide. This software is distributed without any
// warranty.
//
// You should have received a copy of the CC0 Public Domain Dedication along with this software.
// If not, see <http://creativecommons.org/publicdomain/zero/1.0/>.


// may need to support intermediate spacer lengths since McMaster Carr doesn't have a 15mm spacer


//------------------------------------------------------------------
// User Inputs
//------------------------------------------------------------------

/*[Switch Behavior]*/
//force indexes larger than 0 will include a leaf spring
activation_force_index = 0; // [0:10]
//distances larger than 0 require a force index larger than 0
activation_distance = 0; // [0:5]
evaluation_switch = "no"; // [yes,no]

/*[Spacer Info]*/
spacer_length = 15; // [10,15,20]
spacer_thickness = 10;
spacer_screw_length = 10;
spacer_screw_size = "M6"; // [M4,M5,M6]

/*[Microswitch Info]*/
microswitch_type = "black insulation"; // [black insulation,red and black insulation]

/*[Activation Surface]*/
activation_surface_type = "flat"; // [flat,curved]
activation_surface_thickness = 4; // [4:10]
activation_surface_width = 45; // [30,35,40,45,50,55,65,70,75,80,85,90,95,100]
activation_surface_corner_radius = 5; // [5,10,15,20,25,30,35,40,45,50]
activation_surface_facets = 15; // [4:50]

/*[Switch Info]*/
switch_width=65; // [65,70,75,80,85,90,95,100]
switch_corner_radius = 5; // [5,10,15,20,25,30,35,40,45,50]
// print a "hole size test" part to obtain this value
spacer_hole_test_value = 3;// [1,2,3,4,5]  

/*[Special Settings]*/
section = "no"; // [yes,no]
change_headphone_jack_location = 0; // [-3:3]

/*[Parts to Show in Assembly View]*/
show_activation_surface = "yes"; // [yes,no]
show_spacer = "yes"; // [yes,no]
show_switch_cover = "yes"; // [yes,no]
show_spacer_plug = "yes"; // [yes,no]
show_mini_post = "yes"; // [yes,no]
show_leaf_spring = "yes"; // [yes,no]
show_headphone_jack = "yes"; // [yes,no]
show_microswitch = "yes"; // [yes,no]
show_switch_base = "yes"; // [yes,no]
show_switch_mount = "yes"; // [yes,no]

/*[Part to Print]*/
part = "switch base"; // [activation surface, switch cover, switch base, leaf spring, spacer plug, switch mount, leaf spring collection - same activation distance, leaf spring collection - same activation force index, spacer plug collection - part 1, spacer plug collection - part 2, 10 mini-posts, hole size test, assembled switch]




/*[Hidden]*/
$fn=100;
fudge=0.005;


// spacer related measures
bolt_len = spacer_screw_length;
bolt_dia = (spacer_screw_size=="M2")? 2 :
				 (spacer_screw_size=="M3")? 3 :
				 (spacer_screw_size=="M4")? 4 :
				 (spacer_screw_size=="M5")? 5 : 6;
bolt_scale = 1;
threaded_hole_scale = 1.05;


//microswitch variables
microswitch_width = (microswitch_type == "black insulation") ? 18.3 : 15.33; // the short dimension of the microswitch
microswitch_height = (microswitch_type == "black insulation") ? 18.3 : 16.19; //the long dimension of the microswitch
microswitch_thickness = (microswitch_type == "black insulation") ? 5.5 : 7;
button_thickness= (microswitch_type == "black insulation") ? 1.6 : 0;
m_t = microswitch_thickness + button_thickness + 0.5;  // a little slop for safety

button_dia = (microswitch_type == "black insulation") ? 11.25 : 6.77;
slot_width = (microswitch_type == "black insulation") ? 3 : 12;
r1 = (microswitch_type=="black insulation") ? 0 : -45;
r2 = (microswitch_type=="black insulation") ? -90 : 45;
r3 = (microswitch_type=="black insulation") ? 180 : -135;

retainer_height = (microswitch_type=="black insulation") ? 6 : 10;
retainer_thickness = (microswitch_type=="black insulation") ? 2 : 3;
retainer_width = (microswitch_type=="black insulation") ? 10 : 12;
retainer_slot_width = (microswitch_type=="black insulation") ? 0 : 1.5;
retainer_wall_offset = (microswitch_type == "black insulation") ? 3 : 3;


// switch variables
switch_wall_thickness = 2;
switch_top_thickness = 2;
switch_bottom_thickness = 3;
include_leaf_spring = (activation_force_index > 0 || (activation_force_index==0 && activation_distance>0)) ? "yes" : "no";
switch_height = (spacer_length==10 && include_leaf_spring=="no") ? 27 :
				(spacer_length==15 && include_leaf_spring=="no") ? 30 :
				(spacer_length==20 && include_leaf_spring=="no") ? 35 :
				(spacer_length==10 && include_leaf_spring=="yes") ? 30 :
				(spacer_length==15 && include_leaf_spring=="yes") ? 35 :
				(spacer_length==20 && include_leaf_spring=="yes") ? 40 :
				100;
es_switch_height = (spacer_length==10) ? 30 :
				   (spacer_length==15) ? 35 :
				   (spacer_length==20) ? 40 :
				   100;
switch_base_height = (evaluation_switch=="no") ? switch_height-switch_top_thickness : es_switch_height-switch_top_thickness;
pedestal_height = 14 + switch_bottom_thickness;
top_of_microswitch = switch_bottom_thickness + m_t;

switch_fillet = min(switch_corner_radius,switch_width/2-fudge);
headphone_jack_len = 26.5;

v = (microswitch_type=="black insulation") ? 
	[[65,5,-.5],[65,10,-.5],[65,15,.5],[65,20,1],[65,25,4],[65,30,6],[65,35,7],[65,40,8],[65,45,8],[65,50,8],
	[70,5,-3],[70,10,-3],[70,15,-3],[70,20,-2],[70,25,0],[70,30,2],[70,35,4],[70,40,4],[70,45,4],[70,50,4],
	[75,5,-6],[75,10,-6],[75,15,-6],[75,20,-6],[75,25,-5],[75,30,-3],[75,35,0],[75,40,1],[75,45,1],[75,50,1],
	[80,5,-8],[80,10,-8],[80,15,-8],[80,20,-8],[80,25,-7.5],[80,30,-5.5],[80,35,-4],[80,40,-2],[80,45,-2],[80,50,-2],
	[85,5,-10],[85,10,-10],[85,15,-10],[85,20,-10],[85,25,-10],[85,30,-9],[85,35,-8],[85,40,-6],[85,45,-5],[85,50,-5],
	[90,5,-13],[90,10,-13],[90,15,-13],[90,20,-13],[90,25,-12],[90,30,-12],[90,35,-11],[90,40,-10],[90,45,-8],[90,50,-8],
	[95,5,-15],[95,10,-15],[95,15,-15],[95,20,-15],[95,25,-15],[95,30,-15],[95,35,-14.5],[95,40,-13.5],[95,45,-12],[95,50,-11],
	[100,5,-18],[100,10,-17.5],[100,15,-17.5],[100,20,-17.5],[100,25,-17.5],[100,30,-17.5],[100,35,-17.5],[100,40,-16.5],[100,45,-15.5],[100,50,-14]]
	:
	[[65,5,-.5],[65,10,-.5],[65,15,.5],[65,20,1],[65,25,4],[65,30,6],[65,35,7],[65,40,8],[65,45,8],[65,50,8],
	[70,5,-3],[70,10,-3],[70,15,-3],[70,20,-2],[70,25,0],[70,30,2],[70,35,4],[70,40,4],[70,45,4],[70,50,4],
	[75,5,-6],[75,10,-6],[75,15,-6],[75,20,-6],[75,25,-5],[75,30,-3],[75,35,0],[75,40,1],[75,45,1],[75,50,1],
	[80,5,-8],[80,10,-8],[80,15,-8],[80,20,-8],[80,25,-7.5],[80,30,-5.5],[80,35,-4],[80,40,-2],[80,45,-2],[80,50,-2],
	[85,5,-10],[85,10,-10],[85,15,-10],[85,20,-10],[85,25,-10],[85,30,-9],[85,35,-8],[85,40,-6],[85,45,-5],[85,50,-5],
	[90,5,-13],[90,10,-13],[90,15,-13],[90,20,-13],[90,25,-12],[90,30,-12],[90,35,-11],[90,40,-10],[90,45,-8],[90,50,-8],
	[95,5,-15],[95,10,-15],[95,15,-15],[95,20,-15],[95,25,-15],[95,30,-15],[95,35,-14.5],[95,40,-13.5],[95,45,-12],[95,50,-11],
	[100,5,-18],[100,10,-17.5],[100,15,-17.5],[100,20,-17.5],[100,25,-17.5],[100,30,-17.5],[100,35,-17.5],[100,40,-16.5],[100,45,-15.5],[100,50,-14]];

corner_radius_index = [[5,0],[10,1],[15,2],[20,3],[25,4],[30,5],[35,6],[40,7],[45,8],[50,9]];
cri = search(switch_corner_radius,corner_radius_index,0); // e.g., [1]

headphone_jack_start = v[search(switch_width,v,0,0)[cri[0]] ][2] - 2 - change_headphone_jack_location;


// leaf spring variables
max_activivation_distance = (spacer_length>10 || evaluation_switch=="yes") ?  5 : 3;
max_spring_thickness = (spacer_length>10 || evaluation_switch=="yes") ? 3 : 1.5;
a_d = activation_distance;
act_force_vector = [ [0,0], [1,2], [1,4], [1.5,2], [2,2], [1.5,4], [2.5,2], [2,4], [3,2], [2.5,4], [3,4] ];
a_f_i = activation_force_index;
act_force = act_force_vector[a_f_i];
s_t = (a_f_i==0 && activation_distance>0) ? 1 :act_force[0];
post_len = pedestal_height - m_t - switch_bottom_thickness - a_d;


// switch cover variables
switch_cover_height = 10; // determines the amount of overlap between the switch base and cover
sleeve_dia = 15;
brace_thickness = 3;
leaf_retention_post_length = (evaluation_switch=="yes") ? switch_base_height - pedestal_height-3.5 : 3;
				
hole_adjustment = 0.2; //account for printed hole being slightly smaller than specified - extrusion line width?
st_plus = spacer_thickness + hole_adjustment;
hex_hole_dia1 = (st_plus-.2)/cos(30);
hex_hole_dia2 = (st_plus-.1)/cos(30);
hex_hole_dia3 = (st_plus-0)/cos(30);
hex_hole_dia4 = (st_plus+.1)/cos(30); 
hex_hole_dia5 = (st_plus+.2)/cos(30); 

cover_hole_size = (spacer_hole_test_value==1) ? hex_hole_dia1 :
				  (spacer_hole_test_value==2) ? hex_hole_dia2 :
				  (spacer_hole_test_value==3) ? hex_hole_dia3 :
				  (spacer_hole_test_value==4) ? hex_hole_dia4 : 
				                                hex_hole_dia5;


//spacer plug variables
plug_width = 15;

mini_post_length = 7;  // mini post will extend 5 mm below the plug. the hole in the plug is 2 mm deep
mini_post_bottom = switch_bottom_thickness + m_t;
mini_post_top = mini_post_bottom + 5;
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

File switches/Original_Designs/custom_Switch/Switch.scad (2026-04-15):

/* Accessible Switch
(c) 2026 Michael Ryan Hunsaker, M.Ed., Ph.D.
Materials: 
    4 #4 x 5/8" Screws 
        (https://www.amazon.com/dp/B08MTFLXTT)
    ss-3gp Microswitch 
        (https://www.digikey.com/en/products/detail/omron-electronics-inc-emc-div/SS-3GP/664724)
    Mono cable 
        (https://www.digikey.com/en/products/detail/tensility-international-corp/10-00344/2350247)
    Solder
    Soldering Iron
    Designed for 3D Print with PLA Filament
*/
// =============================================
// CUSTOMIZER CONTROLS
// =============================================

// Select what to render
part = "exploded_assembly"; 
// [body, switch_base, flexure_spring, button_top, assembly, exploded_assembly]

// Optional: enable colors in preview (disable for STL export)
use_color = true;

// =============================================
// Flexure Switch Assembly
// Components: switch_base, mount_cylinders, flexure_spring, button_top, body
// =============================================
// --- Global render quality ---
$fn = 256;
// =============================================
// SHARED DIMENSIONS 
// =============================================
// Body inner bore (from base())
body_inner_r = 17.5;
// Radial clearance to avoid rubbing
clearance = 0.5;
// Maximum usable radius
max_r = body_inner_r - clearance;   // 17.0 mm
// =============================================
// MOUNTING SCREW CYLINDERS
// =============================================
cyl_od     = 7;                     // mm
cyl_height = 17;                    // mm
// Position cylinders fully inside body
mount_radius = max_r - cyl_od/2;    // = 13.5 mm
// =============================================
// FLEXURE SPRING 
// =============================================
// Flexure must sit inside bolt circle
outer_radius = mount_radius - 0.8;  // ≈ 12.7 mm
inner_radius   = 5;
arm_width      = 1.8;
thickness      = 0.9; // 0.9 = loose, 1.0 = medium, 1.1 = stiff
num_arms       = 3;
// =============================================
// SCREW + PAD CONSTRAINTS
// =============================================
screw_d = 3.2; // value for #4 screws
// Ensure pads never exceed available radial space
pad_diameter = min(screw_d * 3,
                   (max_r - mount_radius) * 2 - 0.5);
pad_height = thickness * 1.5;
// =============================================
// MODULE: arm_cutout
// =============================================
module arm_cutout(center_angle) {
    eps = 0.02;
    rotate([0, 0, center_angle])
    translate([0, 0, thickness/2])
    linear_extrude(height = thickness + eps, center = true)
        hull() {
            translate([inner_radius, 0])
                circle(d = arm_width, $fn = 64);
            translate([outer_radius - 0.5, 0])
                circle(d = arm_width, $fn = 64);
        }
}
// =============================================
// MODULE: flexure_spring
// 3-arm flexure disc.
// =============================================
module flexure_spring() {
    eps = 0.02;
    difference() {
        // =============================
        // FULL FLEXURE SOLID
        // =============================
        union() {
            // --- Outer rim ---
            difference() {
                cylinder(h = thickness, r = outer_radius);
                translate([0, 0, -eps])
                    cylinder(h = thickness + 2*eps,
                             r = outer_radius - arm_width);
            }
            // --- Inner hub ---
            difference() {
                cylinder(h = thickness, r = inner_radius + arm_width);
                translate([0, 0, -eps])
                    cylinder(h = thickness + 2*eps,
                             r = inner_radius);
            }
            // --- Arms (aligned with screws) ---
            for (i = [0 : num_arms - 1]) {
                arm_cutout(i * 120 + 60);
            }
            // --- Reinforcement pads ---
            for (i = [0 : num_arms - 1]) {
                angle = i * 120 + 60;
                // Main pad
                rotate([0, 0, angle])
                translate([mount_radius, 0, -(pad_height - thickness)/2])
                cylinder(h = pad_height,
                         d = pad_diameter,
                         $fn = 64);
                // Smooth blend into arm
                rotate([0, 0, angle])
                hull() {
                    translate([mount_radius, 0, thickness/2])
                        cylinder(h = eps,
                                 d = pad_diameter,
                                 center = true);
                    translate([mount_radius - arm_width, 0, thickness/2])
                        cylinder(h = eps,
                                 d = arm_width * 1.2,
                                 center = true);
                }
            }
        }
        // =============================
        // SCREW HOLES
        // =============================
        for (i = [0 : num_arms - 1]) {
            rotate([0, 0, i * 120 + 60])
            translate([mount_radius, 0, -eps-1])
            cylinder(h = pad_height+1 + 2*eps,
                     r = screw_d / 2,
                     $fn = 64);
        }
    }
}
// =============================================
// MODULE: mount_cylinders
// Three boss cylinders at 120° on the bolt circle.
// =============================================
module mount_cylinders() {
    for (i = [0 : 2]) {
        rotate([0, 0, i * 120 + 60])   // 60° phase keeps cylinders
        translate([mount_radius, 0, 0]) // between the clip features
        difference() {
            // Solid boss
            cylinder(h = cyl_height, d = cyl_od, $fn = 64);
            // #4 clearance bore — epsilon on height prevents
            // co-planar artifacts at top and bottom faces
            cylinder(h = cyl_height + 0.1, d = screw_d,
                     $fn = 32, center = false);
        }
    }
}

module horizontal_boss(){
    difference() {
    translate([6,-7,-9])rotate([90,0,90])attachment();
    translate([9,0,-4])cube([35,10,10],center=true);
    translate([24,0,4]){cube([10,10,10],center=true);}
    translate([0,0,5]){sphere(10,center=true);}
}
}

// =============================================
// MODULE: base
// Lower shell of the switch body.
// =============================================
module base() {
    difference() {
        cylinder(20.75, 20, 20);
        // Cable / wire channel
        translate([0, -10, 3])
            rotate([90, 0, 0])
            cylinder(21, 4, 4);
        // Flat on bottom
        translate([-3.95, -20, -5])
            cube([7.9, 6, 8]);
        // Inner bore
        translate([0, 0, -5])
        color("red") {
            cylinder(26, 17.5, 17.5);
        }
        translate([0,-.25,2.75])
        rotate([90,90,90])
        cylinder(h = cyl_height+9 + 0.1, d = screw_d,
                         $fn = 32, center = false);
    }
    difference() {
        translate([0,0,13])
        cylinder(12.999, 22.5, 22.5);
            color("red") {
            cylinder(26, 17.5, 17.5);
        } }
    horizontal_boss();
rotate([0,0,120])horizontal_boss();
rotate([0,0,240])horizontal_boss();
}

// =============================================
// MODULE: top
// Upper cap of the switch body.
// =============================================
module top() {
    difference() {
            cylinder(1, 20, 20);
            translate([0, 0, -1])
                cylinder(5, 15, 15);
    }
}
// =============================================
// MODULE: body
// Full switch body = Union of base + top.
// =============================================
module body() {
        union() {
            base();
            translate([0, 0, 25])
                top();
        }
}
// =============================================
// MODULE: button_top
// Uses flexure spring to not rely on tactile switch for recovery
// =============================================
module button_top() {
    difference() {
    union() {
    // Flat base disc
    cylinder(2.5, 17, 17);
    // Button pressing Surface
    translate([0,0,-3])cylinder(h = 4, r = inner_radius + arm_width+1);
    }
    
    translate([0,0,-3.01])   // start from top surface
        hex_bolt_hole(
            thickness = 10,
            af = 5.56,
            head_depth = 3,
            shaft_d = 3.2,
            clearance = 0.2
        );
    }
}   
// =============================================
// MODULE: hex_pocket
// for #4 bolt
// =============================================
af = 5.56;                 // across flats (mm)
clearance = 0.2;           // adjust for print tolerance
hex_d = (af + clearance) / cos(30);
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

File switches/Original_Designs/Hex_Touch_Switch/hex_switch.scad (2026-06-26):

$fn = 32;

/* [Render Part] */
// Which part to render
part = "blowup_assembled"; // [cap_base:Hex Cap Base, cap_cover:Hex Cap Cover, hex_cap_with_ridging:Cap with Ridges, body:Hex Body, spring:spring, assembled:Assembled Switch, blowup_assembled:Assembly Part List, assembly:Full Assembly]

/* [Hidden] */

// ─── Imports ────────────────────────────────────────────────────────────────

module hex_cap_ttp223() {
    color("red") {
        import("hextouch_open_base.stl");
    }
}

module hex_cap_ttp223_cover() {
color("violet"){
    import("hextouch_open_lid_noholes.stl");
}
}
// ─── Sub-components ─────────────────────────────────────────────────────────

module switch_top_slot() {
    difference() {
        translate([0, 0, -1.5]) cylinder(3, 8, 8, center = true, $fn = 6);
        translate([0, 0, -2.2]) cube([4.05, 4.05, 2.75], center = true);
    }
}

// ─── Main assemblies ────────────────────────────────────────────────────────
module switch_hex_cap_cover() {
hex_cap_ttp223();
}

module switch_hex_cap() {
    difference() {
    union() {
        translate([-46,0,0])rotate([0,0,0])color("yellow"){hex_cap_ttp223_cover();}
        switch_top_slot();
    }
    translate([-5,8.5,-5])cube([10,3,20]);
   translate([-8,8.5,-5])cube([15,2,20]);
}
}




module hex_cap_whole() {
translate([0,0,15.5])switch_hex_cap();
rotate([0,0,180])translate([0,0,25])rotate([180,0,0])hex_cap_ttp223();
}

module hex_cap_with_ridging() {
difference() {
rotate([0,0,-120]){hex_cap_whole();}
translate([0,15,0])cube([2,5,85]);
translate([0,-20,0])cube([2,5,85]);

rotate([0,0,60]) {translate([0,15,0])cube([2,5,85]);
translate([0,-20,0])cube([2,5,85]);}

rotate([0,0,-60]) {translate([0,15,0])cube([2,5,85]);
translate([0,-20,0])cube([2,5,85]);}
}
}


module switch_hex_body() {
    side   = 20.7;
    wall   = 1.75;
    height = 18.5;

    difference() {
        // Outer solid
        linear_extrude(height = height)
            offset(delta = wall)
                circle(r = side, $fn = 6);
        // Inner cavity, leaving a 2 mm bottom
        translate([0, 0, wall + 2])
            linear_extrude(height = height)
                circle(r = side, $fn = 6);
        // Side cable hole
        translate([-15, 8.75, 4.5]) rotate([90, 0, 60]) cylinder(75, 3, 3, $fn = 32);
        // Wide Wire Ribbon Hole
        translate([20, -11, 9]) rotate([90, 0, 60]) cube([10,3,15],center=true);
    }

    rotate([0, 0, -30]) {
        difference() {
            translate([0, 0, 3.99999]) cube([10, 10, 4], center = true);
            translate([0,  0,   11.001]) cube([11, 1.5, 3], center = true);          // Wire channel
            translate([0,  3.25, 23.001]) rotate([ 45, 0, 0]) cube([15, 15, 22], center = true); // Ergonomic taper
            translate([0, -3.25, 23.001]) rotate([-45, 0, 0]) cube([15, 15, 22], center = true); // Ergonomic taper
            translate([-.75,  10.0,  4.5]) rotate([90, 0,  0]) cube([1.5, 10, 20]);
            translate([-10, 0,   4.5]) rotate([90, 0, 90]) cylinder(75, 2, 2);
        }
    }
    translate([0,17,8.5])cube([1,2,9]);
    translate([0,-19,8.5])cube([1,2,9]);

    rotate([0,0,60]) {translate([0,17,8.5])cube([1,2,9]);
    translate([0,-19,12.5])cube([1,2,5]);}

    rotate([0,0,-60]) {translate([0,17,8.5])cube([1,2,9]);
    translate([0,-19,8.5])cube([1,2,9]);}
}

module switch_hex_spring()
{
    sp_side   = 14;
    sp_wall   = 1.25;
    sp_height = 14.5;

    spring_h = 3.0;

    // radial clearance at top of spring zone
    clearance = 0.3;   // 0.2–0.4 mm target

    inner_r = sp_side;
    inner_r_top = sp_side + clearance;

    difference()
    {
        // -----------------------
        // OUTER SHELL (unchanged)
        // -----------------------
        linear_extrude(height = sp_height)
            offset(delta = sp_wall)
                circle(r = sp_side, $fn = 6);

        // ----------------------------------------
        // INNER CAVITY WITH RADIAL TAPER (KEY FIX)
        // ----------------------------------------
        union()
        {
            // lower rigid cavity (no clearance)
            translate([0,0,sp_wall -2])
                linear_extrude(height = sp_height+3)
                    circle(r = inner_r, $fn = 6);

            // upper spring zone cavity (expanded)
            translate([0,0,sp_height - spring_h])
                linear_extrude(height = spring_h)
                    circle(r = inner_r_top, $fn = 6);
        }

        // -----------------------
        // SIDE CABLE HOLE
        // -----------------------
        translate([-15, 8.75, 4.5])
            rotate([90, 0, 60])
                cylinder(h = 75, r = 2, $fn = 32);

        // -----------------------
        // RIBBON SLOT
        // -----------------------
        translate([15, -8, 9])
            rotate([90, 0, 60])
                cube([10, 2.5, 15], center = true);
    }
}
// -----------------------------------------
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

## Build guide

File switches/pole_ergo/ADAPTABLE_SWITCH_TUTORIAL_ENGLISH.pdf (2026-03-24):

CC BY-NC-SA pole-ergo.fr - Guy Ehretsmann | 2018
www.pole-ergo.fr | technologie@pole-ergo.fr

THE ADAPTABLE SWITCH

INTRODUCTION

The switch is an accessible push button widely used in the field of disability. It is designed to facilitate access to different types of technologies and, in an extensive way, to allow the user to act on his environment.

It transforms a motor gesture, lacking precision, into, for example, a signal that can be used by a computer, a tablet or a telephone to fully control them when they are set for this operating mode.

The switch also gives access to electric toys, communication devices or devices controlled by buttons such as cameras, game consoles, etc....

The switches are available from specialist dealers. There are different sizes, colors but also different types and shapes. However, the contactor can be difficult to choose so many different models and remains, for a majority of models, expensive.

This is why it may be appropriate to have an adaptable switch that can be modified according to the user's motor characteristics, habits or tastes while making it more accessible.

The adaptable switch presented here offers a series of possibilities and customization options that make it potentially capable of responding to all situations.

Totally printed using a 3D printer, the different parts that make it up are assembled like Lego bricks. It offers different mounting and positioning possibilities using the standard used for GOPRO mini cameras, for which accessories are available at low prices everywhere.

It also has a specific button with screw fasteners that allows the manufacture and use of specific custom buttons thus providing a basis for creating unique models to meet nongeneric needs.

Finally, the assembly of the switch is simple and requires only two simple tin solderings which it is possible to avoid, when one does not have soldering iron, by carrying out a simple crimping of wires.

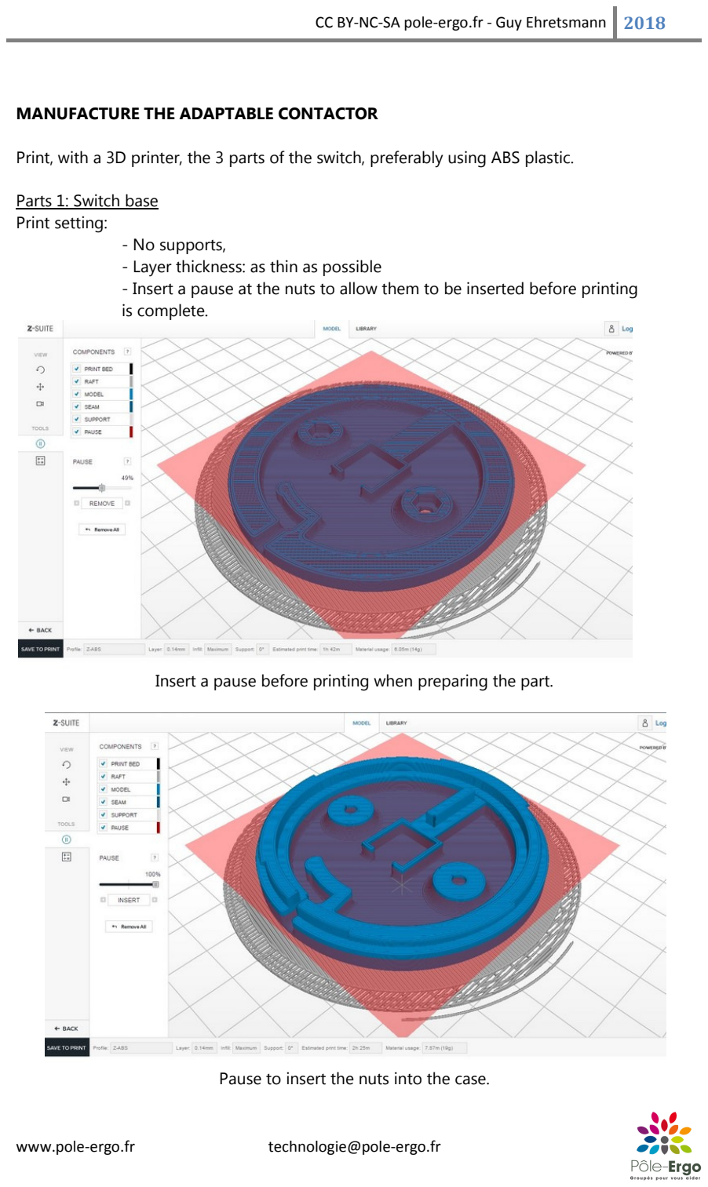
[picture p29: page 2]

MANUFACTURE THE ADAPTABLE CONTACTOR

Print, with a 3D printer, the 3 parts of the switch, preferably using ABS plastic.

Parts 1: Switch base
Print setting:
- No supports,
- Layer thickness: as thin as possible
- Insert a pause at the nuts to allow them to be inserted before printing is complete.

Insert a pause before printing when preparing the part.

Pause to insert the nuts into the case.

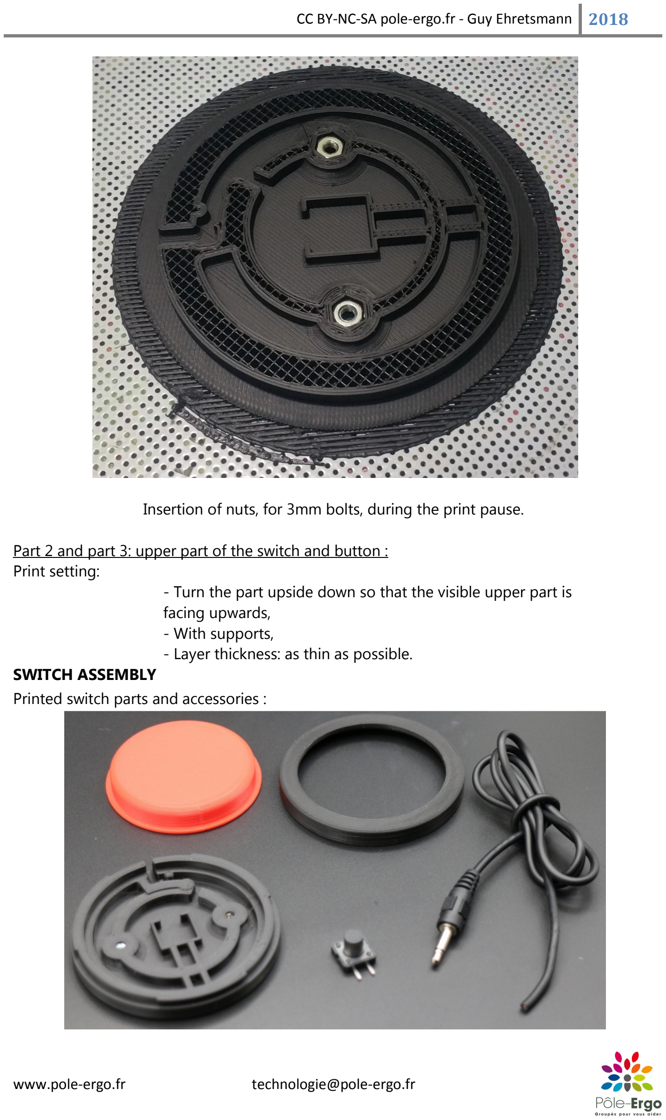
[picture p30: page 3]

Insertion of nuts, for 3mm bolts, during the print pause.

Part 2 and part 3: upper part of the switch and button : Print setting:
- Turn the part upside down so that the visible upper part is facing upwards,
- With supports,
- Layer thickness: as thin as possible.

SWITCH ASSEMBLY
Printed switch parts and accessories :

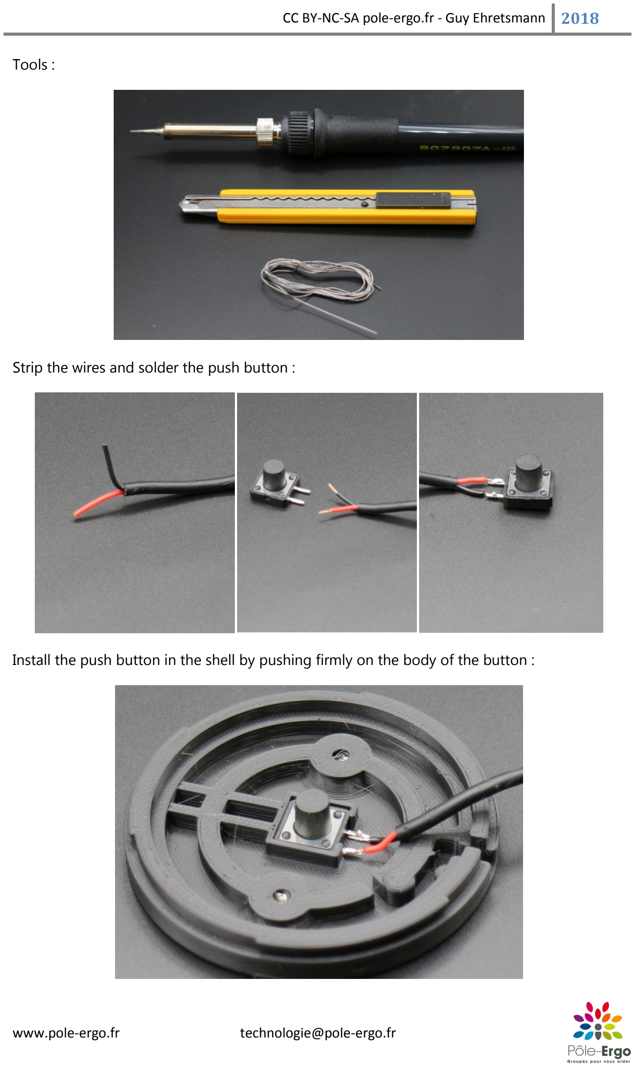
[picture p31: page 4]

Tools :

Strip the wires and solder the push button :

Install the push button in the shell by pushing firmly on the body of the button :

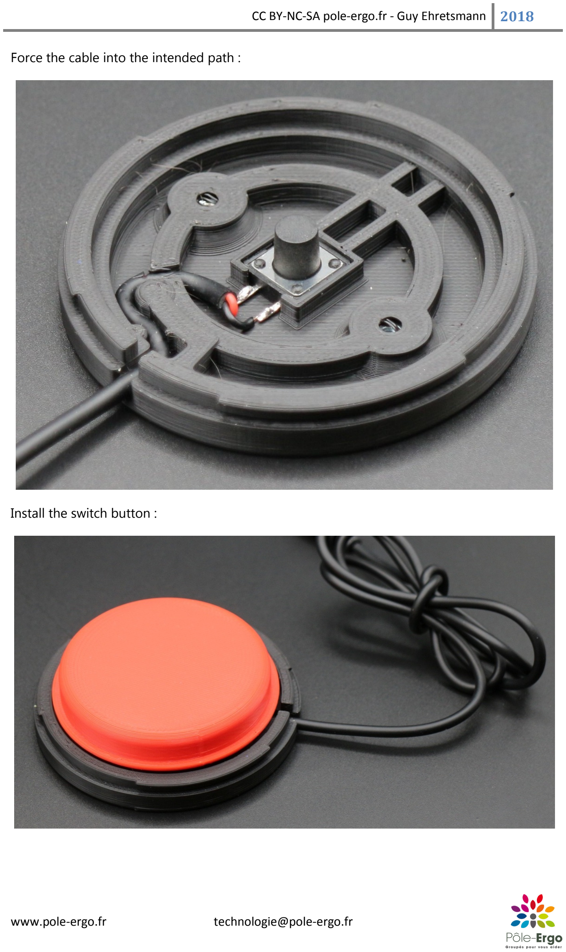
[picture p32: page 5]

Force the cable into the intended path :

Install the switch button :

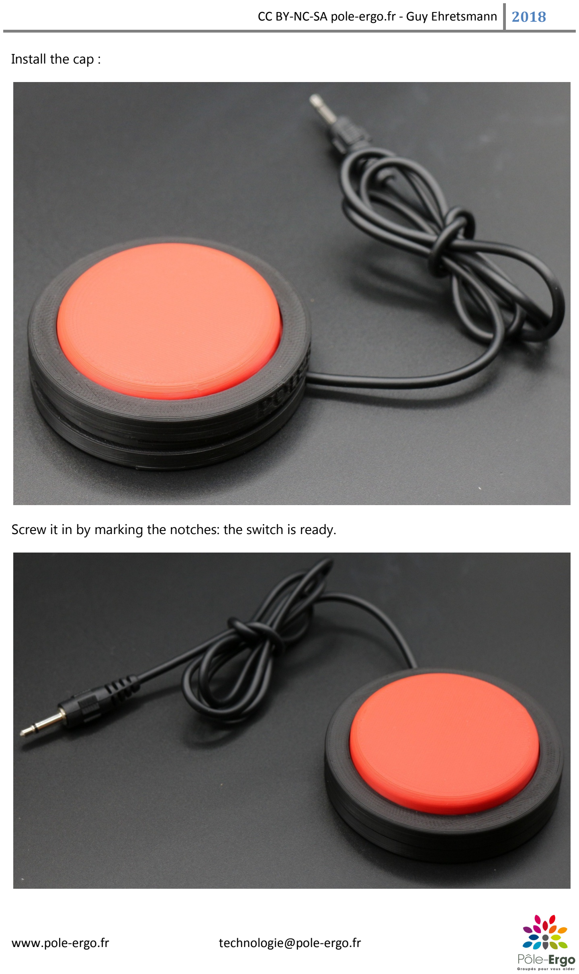
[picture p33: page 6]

Install the cap :

Screw it in by marking the notches: the switch is ready.

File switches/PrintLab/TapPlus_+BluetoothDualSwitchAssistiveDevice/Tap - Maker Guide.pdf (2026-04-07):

# Maker Guide

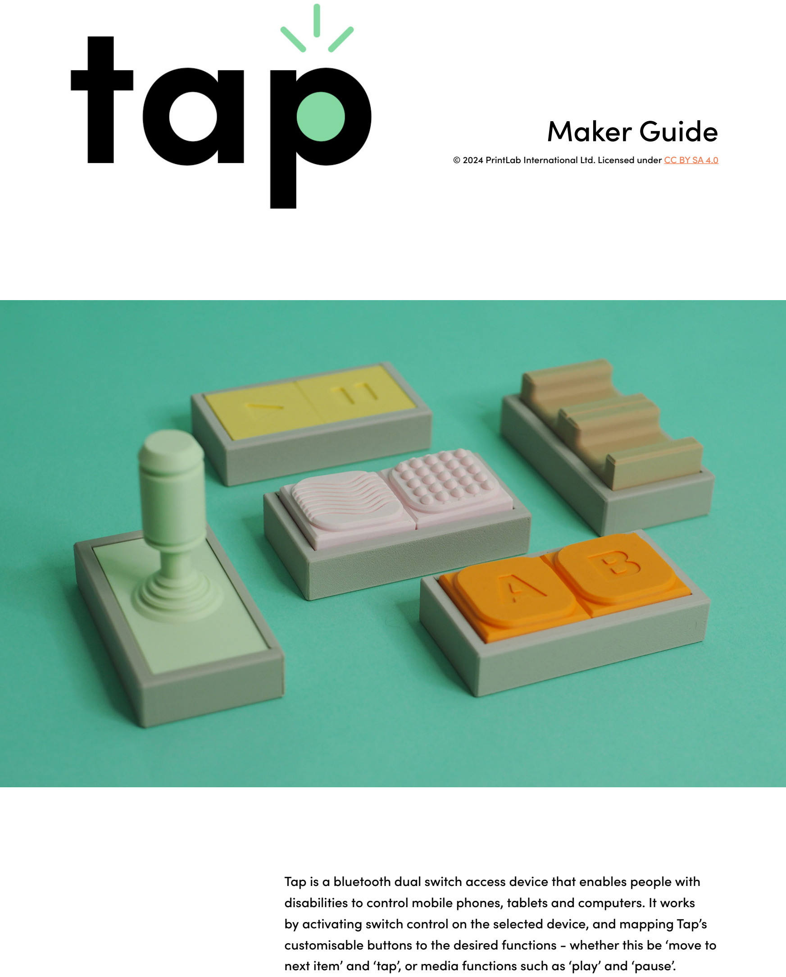
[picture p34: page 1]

Tap is a bluetooth dual switch access device that enables people with disabilities to control mobile phones, tablets and computers. It works by activating switch control on the selected device, and mapping Tap’s customisable buttons to the desired functions - whether this be ‘move to next item’ and ‘tap’, or media functions such as ‘play’ and ‘pause’.

© 2024 PrintLab International Ltd. Licensed under CC BY SA 4.0 (https://creativecommons.org/licenses/by-sa/4.0/)

Computer devices and systems are vital for communication, education, employment, social interaction, and more. But more often than not, they can be inaccessible for people with disabilities.

Tap is designed for people who have limited hand mobility and struggle to use traditional input methods for computer devices, such as keyboard and mouse, small buttons or touchscreens.

It aims to empower individuals with physical and cognitive impairments to interact with technology, engage with their surroundings, and enhance their independence.

Unlike other existing solutions in the market, Tap is affordable, highly customisable and open source.

# why?

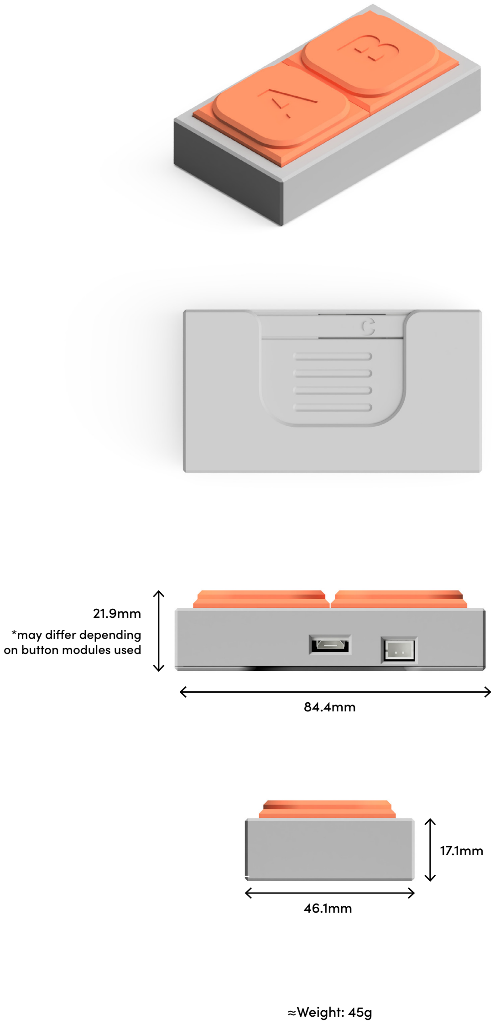
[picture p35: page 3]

84.4mm

46.1mm

17.1mm

21.9mm
*may differ depending
on button modules used

≈Weight: 45g

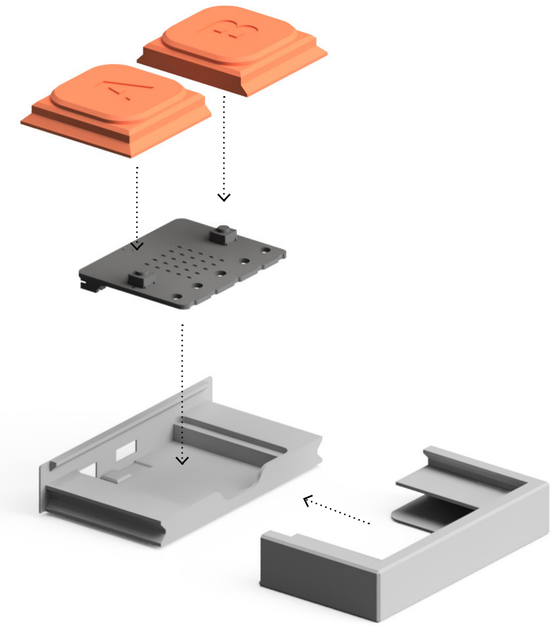
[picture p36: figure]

A micro:bit v2 pocket-sized computer sits at the heart of the device. It is programmed so that when the bluetooth connection is active and the A button is pressed, it sends the keyboard ‘tab’ key as an output. Similarly, when the B button is pressed, it sends the keyboard ‘enter’ key as an output.

By activating switch control on any android, iOS or chromebook device, these inputs can be mapped to various functions such as ‘move to next item’ and ‘tap’, or media functions such as ‘play’ and ‘pause’.

The micro:bit’s existing buttons are transformed into larger accessible buttons through the use of 4 3D printed components. These include a case, sliding lid, and 2 buttons that sit directly on top of the existing buttons. When pushed, they simply press down and activate the existing buttons.

# how?

# materials

Micro:bit v2 with Battery Pack

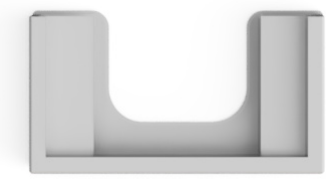
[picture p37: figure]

3D Printed Sliding Lid

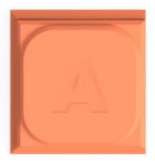
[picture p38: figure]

3D Printed A Button

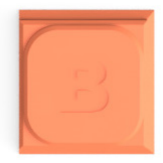
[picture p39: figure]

3D Printed A Button

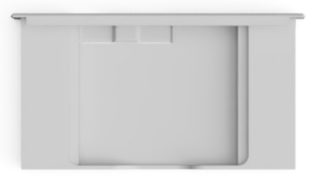
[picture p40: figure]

3D Printed Cradle

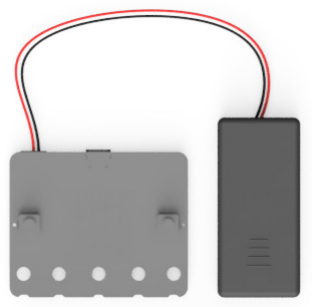
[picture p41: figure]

Example Option:

*Alternatively, you can replace the battery pack with a USB type-B cable to power from your device.

*Multiple options available - see next page

*Multiple options available - see next page

1

1

1

1

1

$19.95

$0.30
(PLA material cost)

$0.33
(PLA material cost)

$0.17
(PLA material cost)

$0.17
(PLA material cost)

https://bit.ly/4djc88I

Description | Qty Required | ≈ Cost (USD)

# button options

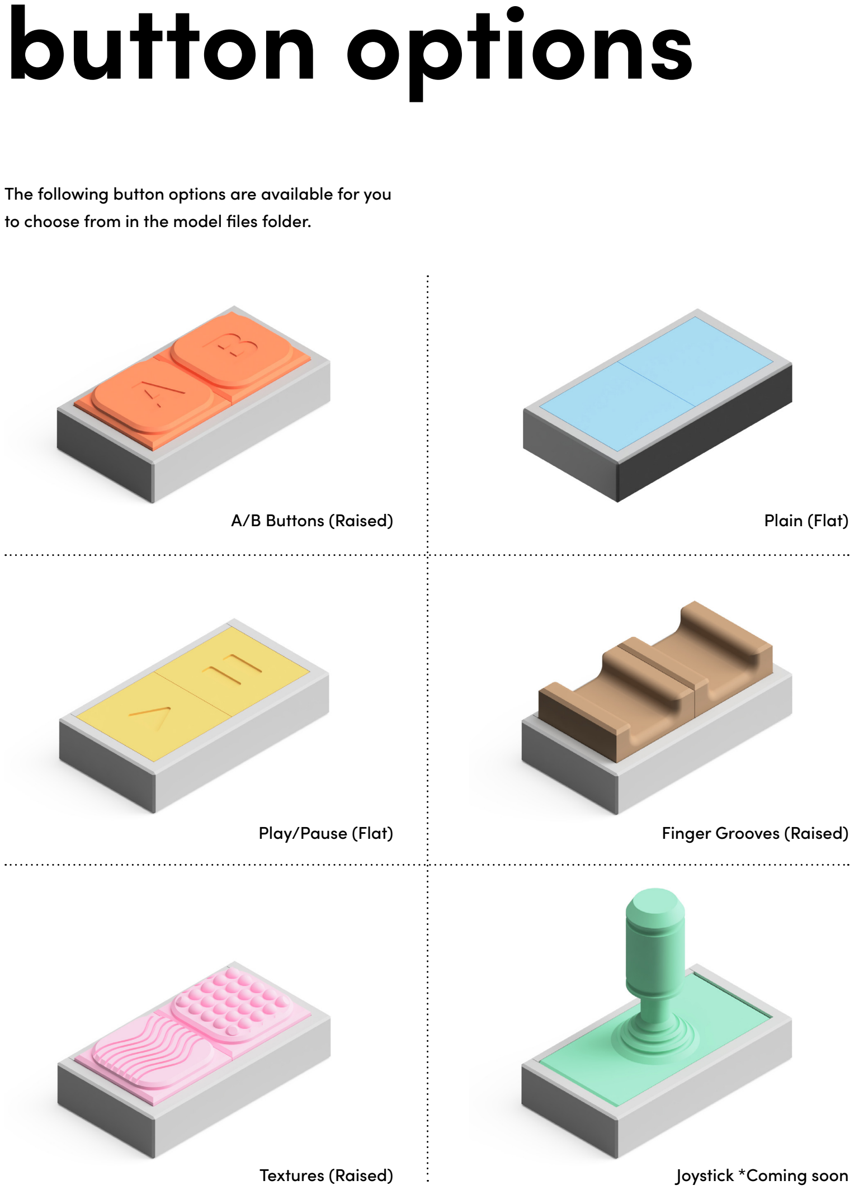
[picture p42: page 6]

The following button options are available for you to choose from in the model files folder.

A/B Buttons (Raised) | Plain (Flat)
Textures (Raised) | Joystick *Coming soon
Play/Pause (Flat) | Finger Grooves (Raised)

# 3d printing

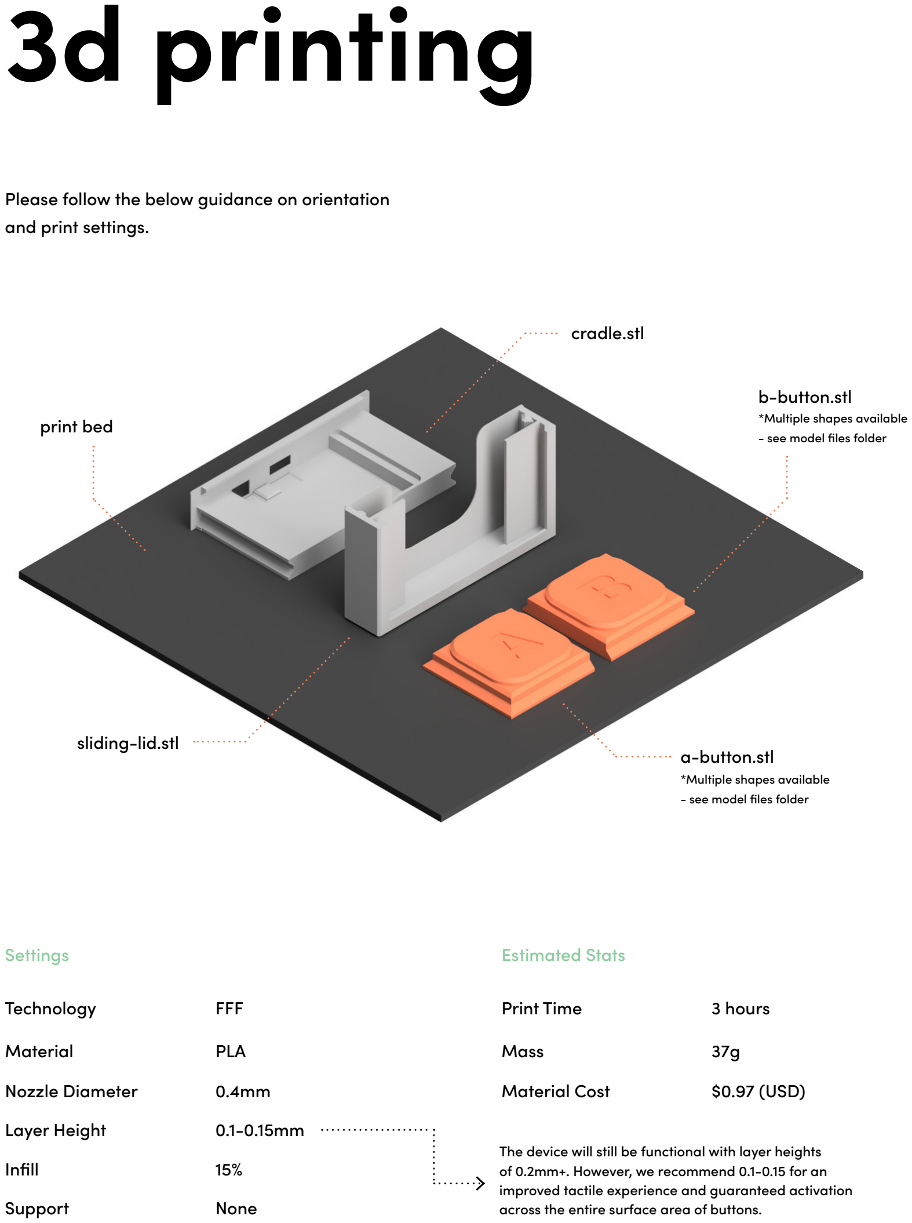
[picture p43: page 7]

print bed

b-button.stl

a-button.stl

cradle.stl

sliding-lid.stl

Please follow the below guidance on orientation and print settings.

Layer Height

Nozzle Diameter | Material Cost
Material | Mass
Technology | Print Time

Infill
Support

0.1-0.15mm
The device will still be functional with layer heights
of 0.2mm+. However, we recommend 0.1-0.15 for an improved tactile experience and guaranteed activation across the entire surface area of buttons.
0.4mm | $0.97 (USD)
PLA | 37g
FFF | 3 hours

15%
None
Settings | Estimated Stats

*Multiple shapes available
- see model files folder

*Multiple shapes available
- see model files folder

Due to the varying tolerances of 3D printers and material properties, we cannot guarantee the same functionality or tactile experience for each manufactured Tap device.

If you have any issues with 3D printing or usage, please contact hello@weareprintlab.com and we will do our best to advise you with alternative print settings or design adjustments.

# disclaimer

# assembly

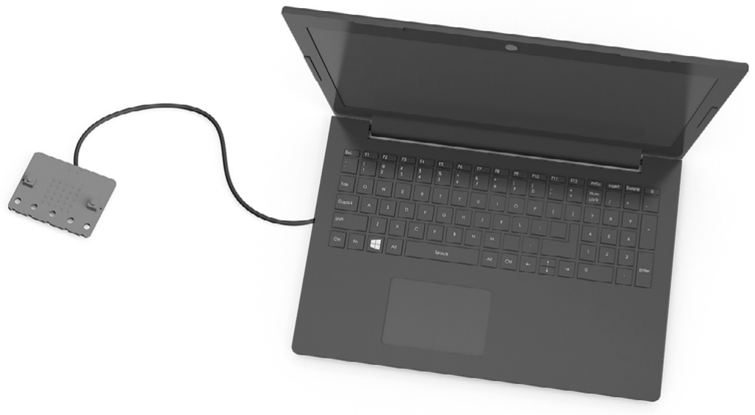
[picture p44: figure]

01.

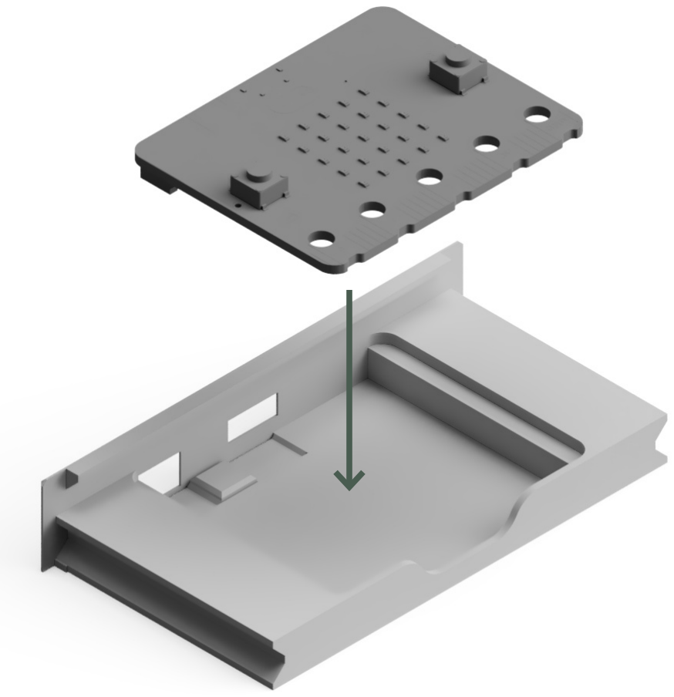
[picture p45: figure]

02.

Connect your micro:bit to a computer via USB connection. Then copy the tabEnterOutput.hex file from the model files folder and paste it onto the micro:bit, just like you would copy and paste a file onto a USB stick!

Place the micro:bit into the 3D printed cradle with the LED side pointing upwards. When placing, tilt the micro:bit so the connection ports feed through the holes in the cradle first.

03.

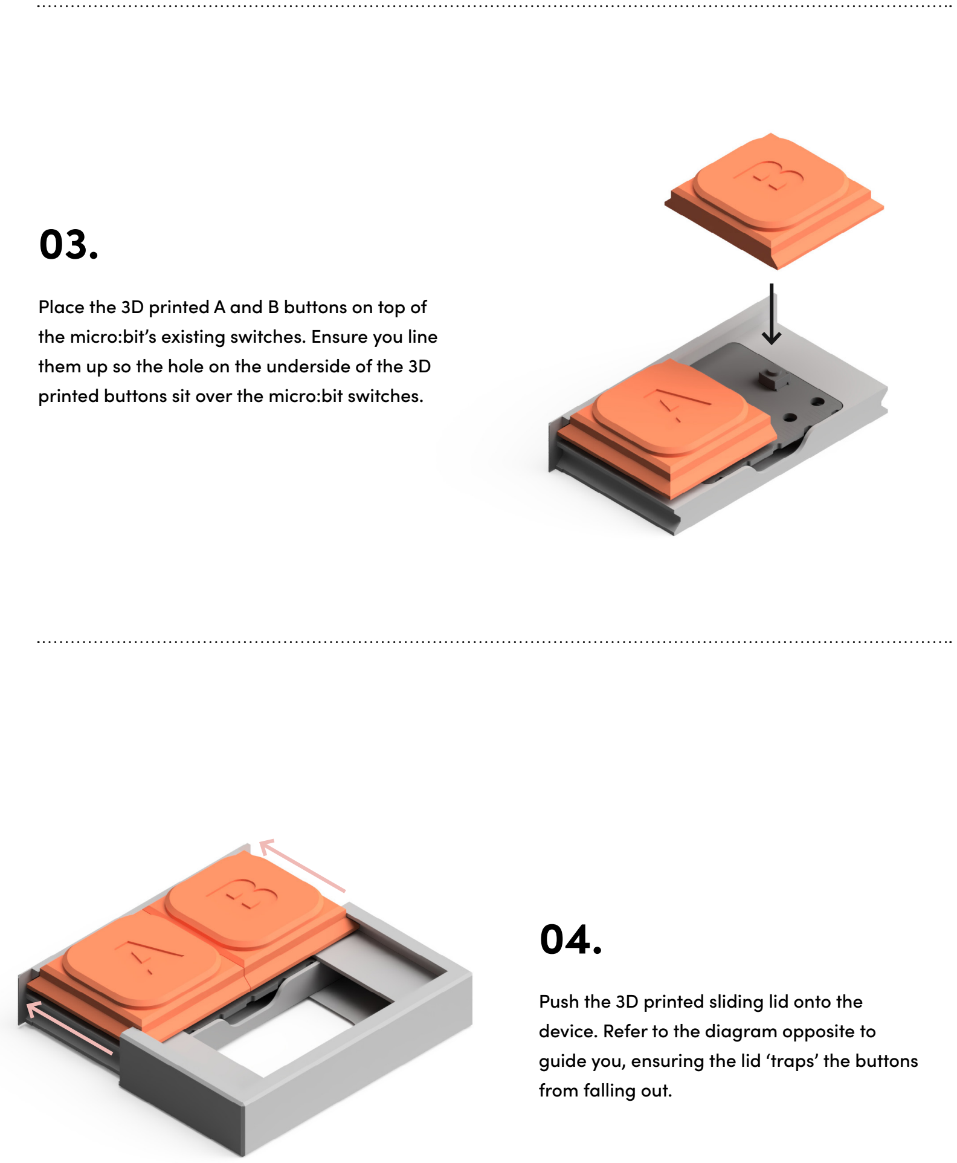
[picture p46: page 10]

04.

Place the 3D printed A and B buttons on top of the micro:bit’s existing switches. Ensure you line them up so the hole on the underside of the 3D printed buttons sit over the micro:bit switches.

Push the 3D printed sliding lid onto the device. Refer to the diagram opposite to guide you, ensuring the lid ‘traps’ the buttons from falling out.

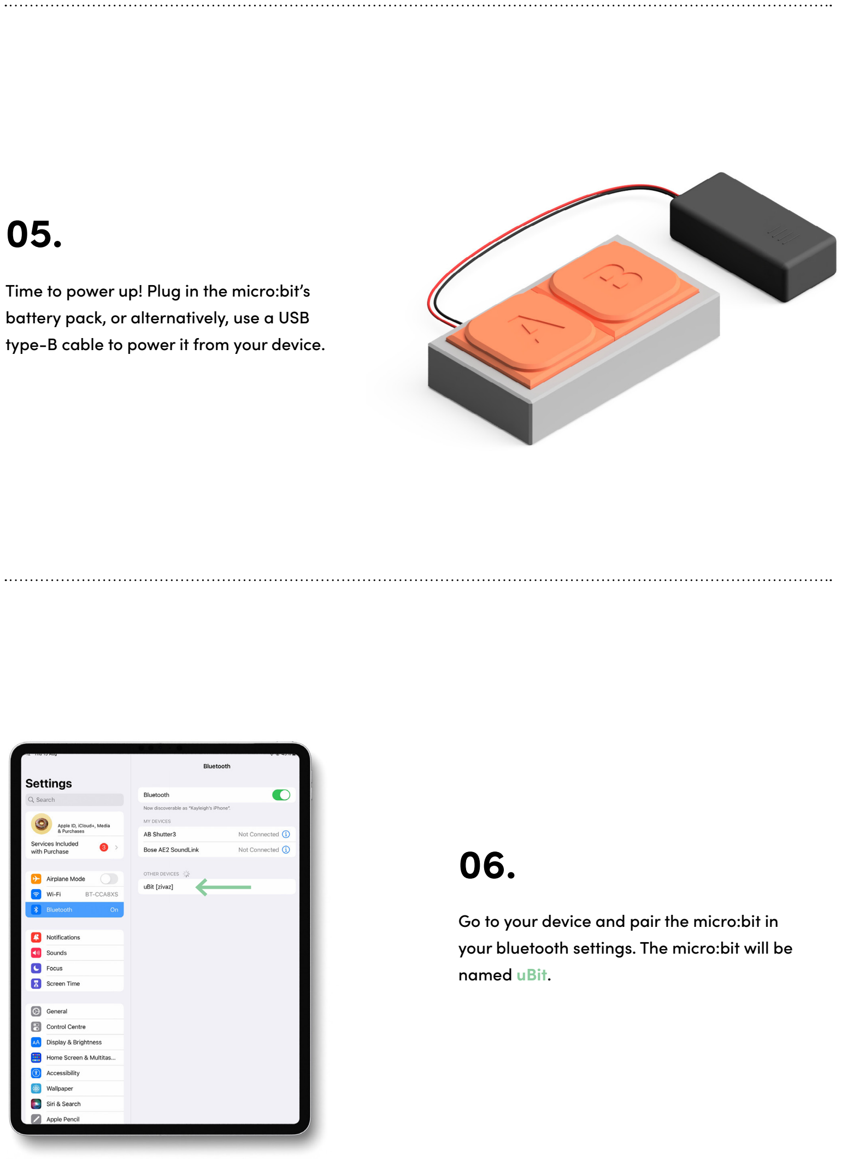
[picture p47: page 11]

05.

06.

Time to power up! Plug in the micro:bit’s battery pack, or alternatively, use a USB type-B cable to power it from your device.

Go to your device and pair the micro:bit in your bluetooth settings. The micro:bit will be named uBit.

The next part of the assembly instructions involves activating switch access on your mobile, tablet or computer device. The instructions in this guide will show you how to set up ‘manual scanning’ on an iPad device with iOS. This will map the A button to the action ‘Move to Next Item’, and the B button to ‘Tap’. If you are using a different device, the steps will be similar, and below are some external links with further information.

Switch Access for Android: https://bit.ly/3X4ZxjQ
Switch Access for Chromebook: https://bit.ly/4dr5AVG

Depending on your requirements, you can also map the A and B buttons to different actions, such as controlling media with play and pause actions. Feel free to experiment with the options on your device!

# switch access

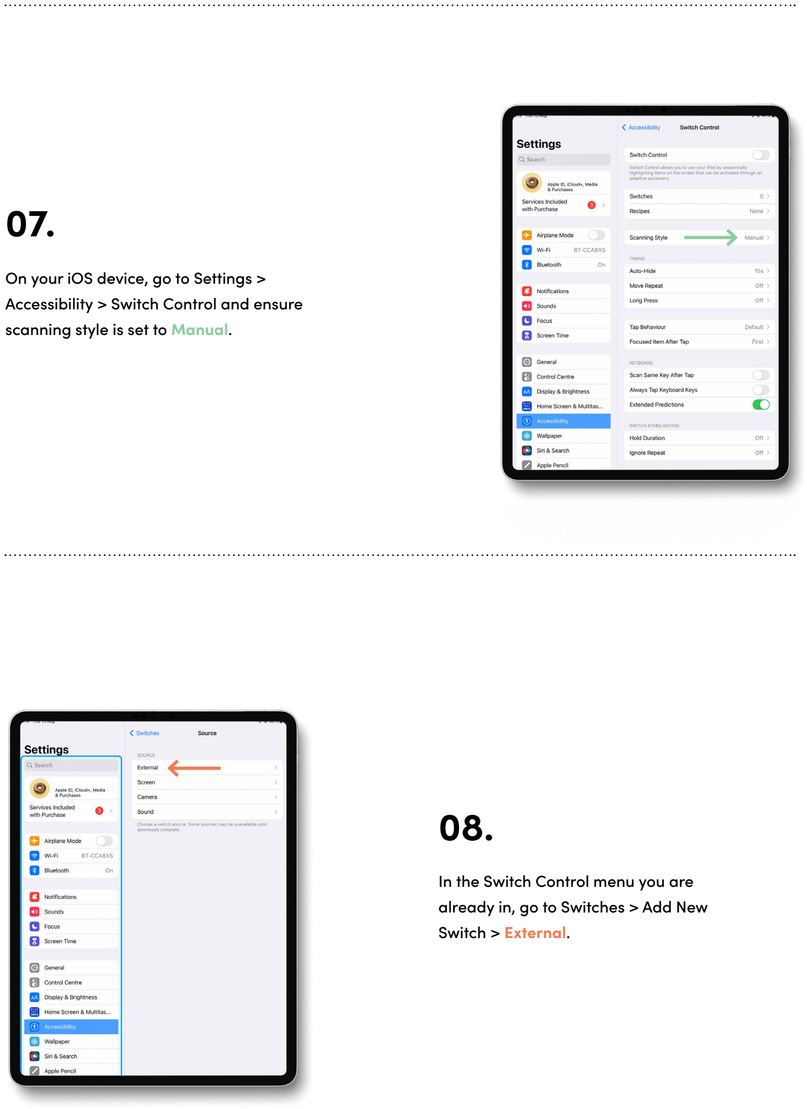
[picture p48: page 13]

07.

08.

On your iOS device, go to Settings > Accessibility > Switch Control and ensure scanning style is set to Manual.

In the Switch Control menu you are already in, go to Switches > Add New Switch > External.

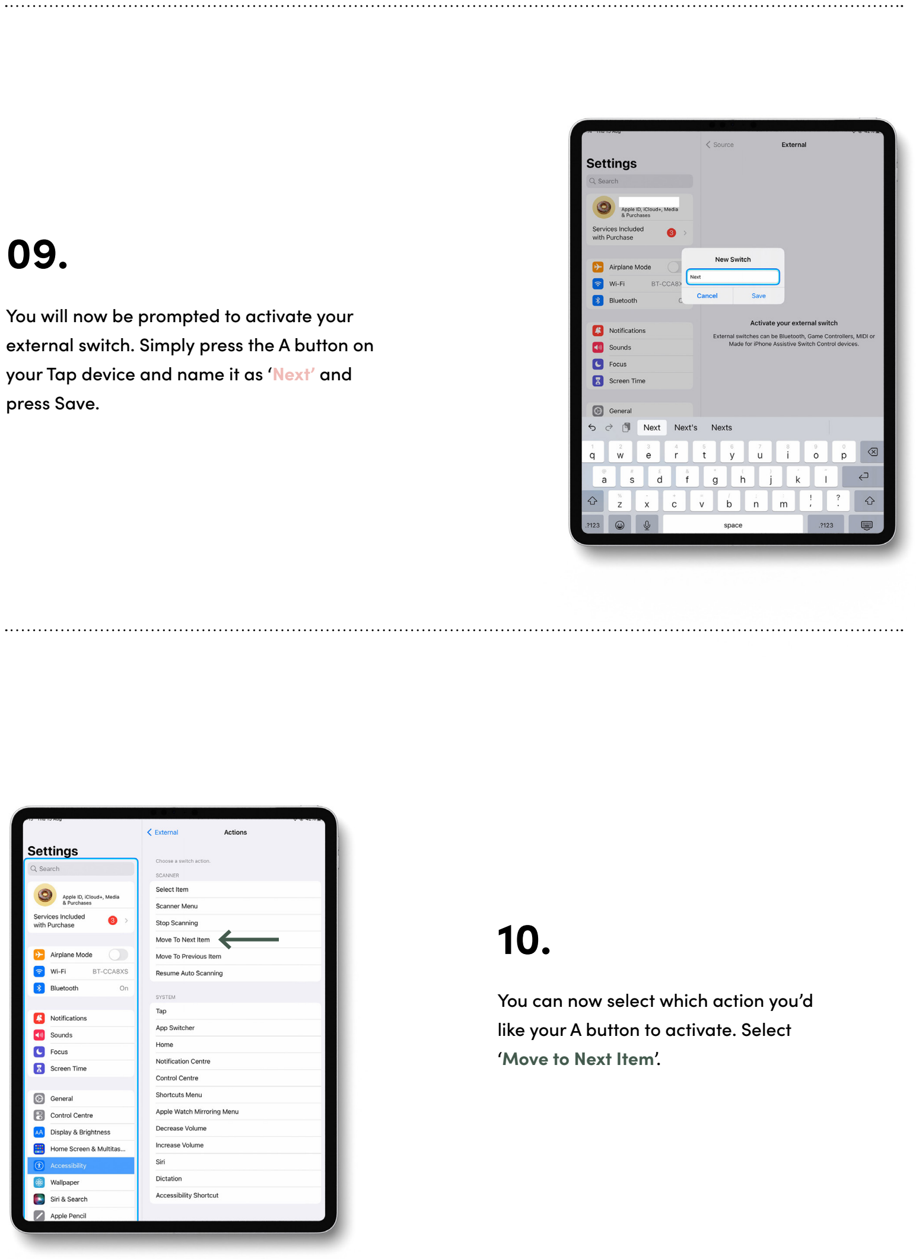
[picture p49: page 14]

09.

10.

You will now be prompted to activate your external switch. Simply press the A button on your Tap device and name it as ‘Next’ and press Save.

You can now select which action you’d like your A button to activate. Select ‘Move to Next Item’.

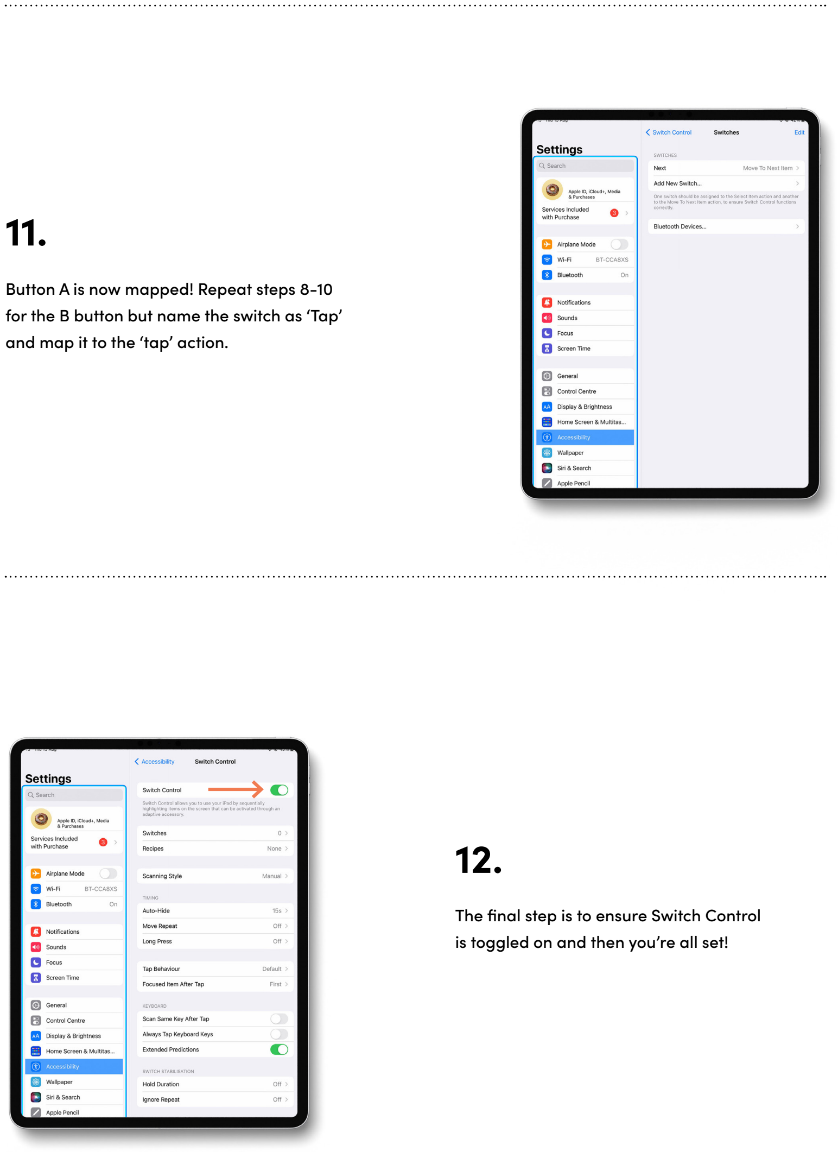
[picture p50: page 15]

11.

12.

Button A is now mapped! Repeat steps 8-10 for the B button but name the switch as ‘Tap’ and map it to the ‘tap’ action.

The final step is to ensure Switch Control is toggled on and then you’re all set!

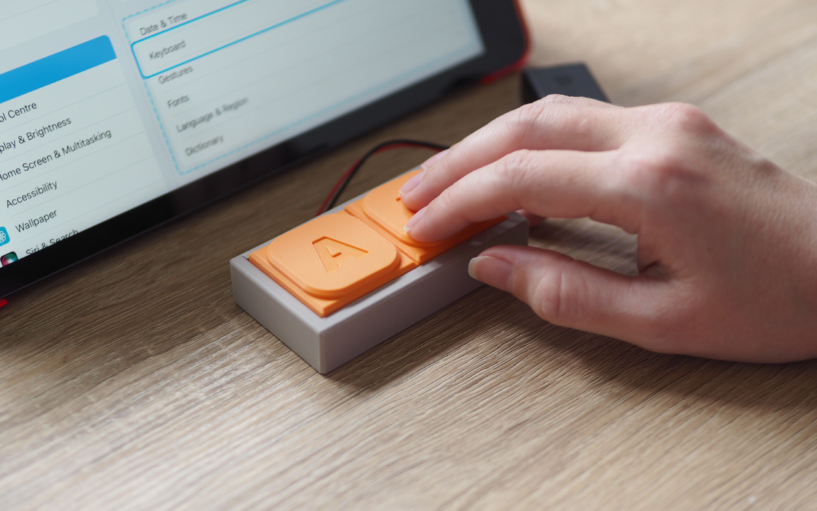
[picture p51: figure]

When switch control is activated, you’ll see a blue border highlighting an item or a group of items. Pressing the A button will change what items are highlighted and once you reach the desired items, press the B button to select. To power off Tap, press and hold the flexure button on the underside of the device for 5 seconds. To power it up again, press the same button once.

# usage

Due to the varying tolerances of 3D printers, you may find that the sliding lid is either too loose or too tight. If this is the case, follow the below instructions to edit the 3D CAD model and reprint the cradle.

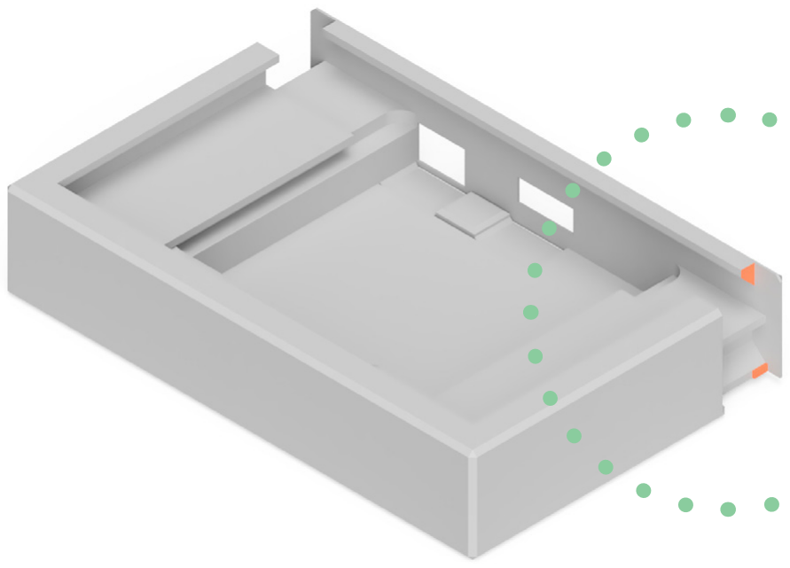
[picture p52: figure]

The lid was designed with a relatively loose fit when it slides over the buttons. As it reaches the top of the cradle, it meets 2 parts on each side (highlighted below), which stick out and apply tight friction to keep the lid in place during use. We call these parts ‘bumps’, and the distance they stick out is easily editable.

The default bump value is 0.4mm. If the sliding lid was a little loose, we recommend changing this to 0.6mm. And if it was a little tight, we recommend changing it to 0.2mm.

To change the bump value, download Autodesk Fusion (https://www.autodesk.com/uk/products/fusion-360/overview) (free for education and personal use) and open the file Tap.f3d from the model files folder. In the modify menu, select Change Parameters. Then click in the Bump Expression field and change the value. Changing the value will automatically update the design with either a larger or smaller bump.

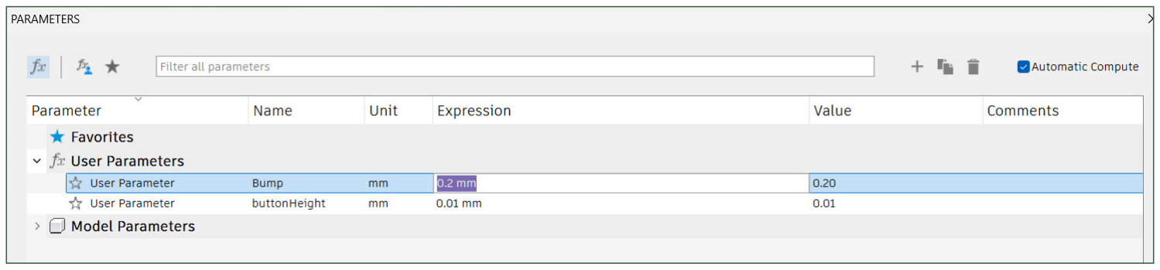
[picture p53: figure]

Once the bump value is changed, you can right-click on the Cradle body in the browser on the left side of the screen and select ‘Save as Mesh’, before saving out a new STL file to 3D print and test.

# adjustments

How the Lid Works

Editing the Bump Value

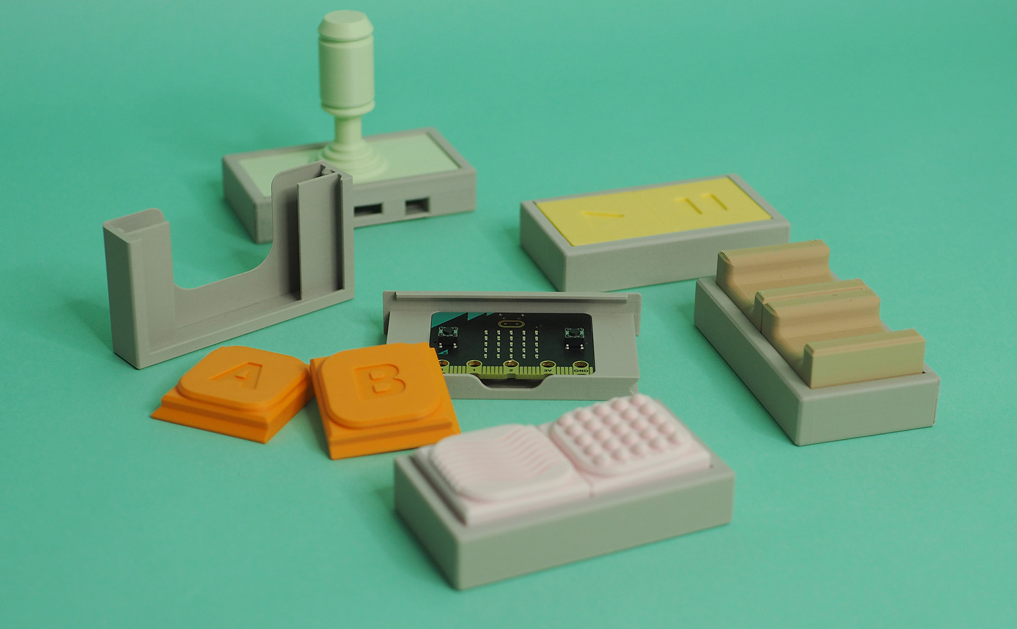
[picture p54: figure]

The Tap design files have been released under a Creative Commons CC BY SA 4.0 (https://creativecommons.org/licenses/by-sa/4.0/) License, whereby we encourage people to modify, adapt and improve the design as they see fit. We are particularly interested in physical modifications, such as mounting solutions, as well as code modifications that might integrate additional functionality. If you have any feedback or suggestions, please email them to hello@weareprintlab.com.

# evolution

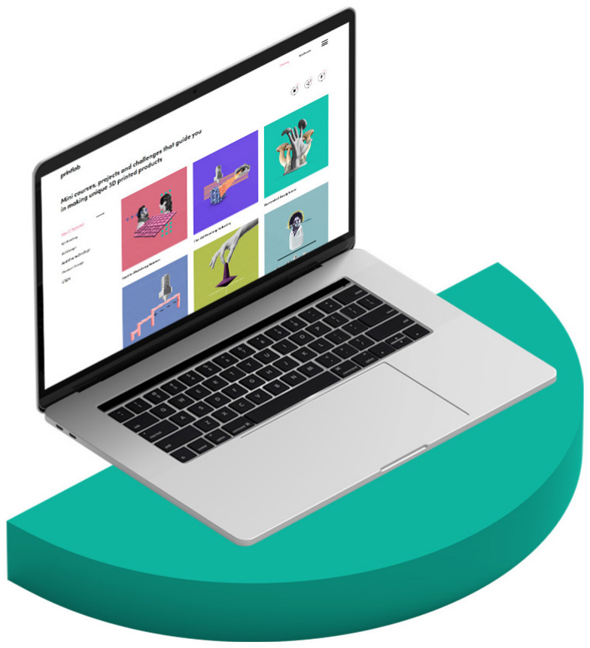
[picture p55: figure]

Want to learn how to use 3D CAD and 3D printing to design your own unique version of Tap? Check out the full course on PrintLab, where we guide you through each step of the design process to make a custom version for a specific end user of your choice.

Course Link: www.weareprintlab.com/projects/at-dual-switch

# learn

# www.weareprintlab.com

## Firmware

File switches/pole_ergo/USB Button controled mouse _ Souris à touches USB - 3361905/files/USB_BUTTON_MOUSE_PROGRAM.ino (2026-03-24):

// Programme par pole-ergo : www.pole-ergo.fr Librement adapté d'exemples proposés par PRJC fabricant de Teensy
// Programme contacteur sur TEENSY 2.0 pour le contacteur proposé sur Thingiverse https://www.thingiverse.com/Pole_ergo/about
// Fonction : emulation des déplacements du pointeur de souris et du clic gauche.
// Installer puis Programmer votre Teensy : voir https://www.pjrc.com/teensy/first_use.html
// Utiliser l'environnement Arduino : voir https://www.arduino.cc/en/Guide/HomePage
// Ecrit et compilé sur IDE Arduino 1.8.5
// Librairies Teensy
// Type de carte : Teensy 2.0 - USB type : Keyboard + Mouse + Joystick - CPU speed : 16MHZ - Keyboard layout : français

//******************** Début de programme *****************************************************
#include <Bounce.h> //utilisation de la librairie Bounce : voir https://www.pjrc.com/teensy/td_libs_Bounce.html

Bounce clic = Bounce(PIN_D5, 10);
Bounce jack1 = Bounce(PIN_D1, 10);
Bounce jack2 = Bounce(PIN_D3, 10);
Bounce jack3 = Bounce(PIN_D4, 10);
Bounce jack4 = Bounce(PIN_D7, 10);

//VARIABLES
int xpos;
int ypos;


//********************** Définition des entrées/sorties du Teensy *****************************

void setup() {
 
  pinMode(PIN_D5, INPUT_PULLUP);  // Défini le bouton poussoir en entrée sur la broche D5 avec resistance interne activée
  pinMode(PIN_D1, INPUT_PULLUP);  // Défini le bouton poussoir en entrée sur la broche D5 avec resistance interne activée
  pinMode(PIN_D3, INPUT_PULLUP);  // Défini le bouton poussoir en entrée sur la broche D5 avec resistance interne activée
  pinMode(PIN_D4, INPUT_PULLUP);  // Défini le bouton poussoir en entrée sur la broche D5 avec resistance interne activée
  pinMode(PIN_D7, INPUT_PULLUP);  // Défini le bouton poussoir en entrée sur la broche D5 avec resistance interne activée
  pinMode(PIN_D6, OUTPUT);        // Défini la LED sur le Teensy sur la broche D6
xpos=0;
ypos=0;
}

//********************** Programme en boucle **************************************************

void loop() {
  clic.update();                    //lecture en boucle de l'entrée "clic" (broche D5 du Teensy)
  jack1.update();                   //lecture en boucle de l'entrée "jack1" (broche D5 du Teensy)
  jack2.update();                   //lecture en boucle de l'entrée "jack2" (broche D5 du Teensy)
  jack3.update();                   //lecture en boucle de l'entrée "jack3" (broche D5 du Teensy)
  jack4.update();                   //lecture en boucle de l'entrée "jack4" (broche D5 du Teensy)

//********************** CLIC SOURIS ET DEPLACMENTS SOURIS*************************************
//  Transforme l'appui du bouton en clic gauche de souris *************************************
//  Transforme l'appui des boutons branchés sur les prises jack en déplacements de pointeurs Jack1 : vers la droite, jack2 vers la gauche, jack3 vers le haut, jack4 vers le bas.
//  Pour augmenter la vitesse de déplacement, modifier les lignes xpos=xpos+2 par +3 ou +4

if (clic.fallingEdge()) {                   // Lorsque l'appui est détecté alors génère un clic gauche par la prise USB
        Mouse.press(MOUSE_LEFT);
            digitalWrite(PIN_D6, HIGH);     // Allume la led rapidement pour confirmer la prise en compte de l'appui sur le bouton
      }

if (jack1.fallingEdge()) {                   // Lorsque l'appui est détecté génère un déplacement vers la droite du pointeur de souris par la prise USB
        xpos=xpos+2;
            digitalWrite(PIN_D6, HIGH);     // Allume la led rapidement pour confirmer la prise en compte de l'appui sur le bouton
      }

if (jack2.fallingEdge()) {                   // Lorsque l'appui est détecté génère un déplacement vers la gauche du pointeur de souris par la prise USB
        xpos=xpos-2;
            digitalWrite(PIN_D6, HIGH);     // Allume la led rapidement pour confirmer la prise en compte de l'appui sur le bouton
      }

if (jack3.fallingEdge()) {                   // Lorsque l'appui est détecté génère un déplacement vers le haut du pointeur de souris par la prise USB
        ypos=ypos+2;
            digitalWrite(PIN_D6, HIGH);     // Allume la led rapidement pour confirmer la prise en compte de l'appui sur le bouton
      }

if (jack4.fallingEdge()) {                   // Lorsque l'appui est détecté génère un déplacement vers le bas du pointeur de souris par la prise USB
        ypos=ypos-2;
            digitalWrite(PIN_D6, HIGH);     // Allume la led rapidement pour confirmer la prise en compte de l'appui sur le bouton
      }
 
      Mouse.move (xpos , ypos);             // Applique le déplacement au pointeur de souris.
      delay(25);

if (jack1.risingEdge()) {                   // Lorsque l'appui est relaché, remet le compteur de déplacements à zero
        xpos=0;
            digitalWrite(PIN_D6, LOW);      // Eteint la led

      }

if (jack2.risingEdge()) {                   // Lorsque l'appui est relaché, remet le compteur de déplacements à zero
        xpos=0;
            digitalWrite(PIN_D6, LOW); 

}
if (jack3.risingEdge()) {                   // Lorsque l'appui est relaché, remet le compteur de déplacements à zero
        ypos=0;
            digitalWrite(PIN_D6, LOW); 

      }
if (jack4.risingEdge()) {                   // Lorsque l'appui est relaché, remet le compteur de déplacements à zero
        ypos=0;
            digitalWrite(PIN_D6, LOW); 

      }
      
if (clic.risingEdge()){                     // Détecte lorsque le bouton poussoir est relaché
        Mouse.release(MOUSE_LEFT);
             digitalWrite(PIN_D6, LOW);     // Eteint la led
  }

  
}

//************************************FIN*************************************************

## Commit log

2026-03-24 preliminary list
    [submodules.csv]
2026-04-07 Added more models from outside GitHub
    [a-button.stl, b-button.stl, cradle.stl, finger-groove-left.stl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]
2026-04-15 Added a personal project into the mix
    [12mm_switch_panel_mount-casing.stl, 12mm_switch_panel_mount-latch.stl, 1corredera.stl, 2058_DIP_SWITCH.stl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]
2026-06-03 added my own models
    [10pin.stl, 12mm_switch_panel_mount-casing.stl, 12mm_switch_panel_mount-latch.stl, 1corredera.stl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]
2026-06-09 added freedcad work
    [BT_SWITCH_HOUSING_chamfered-Box.3mf, BT_SWITCH_HOUSING_chamfered-Box.stl, BT_SWITCH_HOUSING_chamfered.FCStd, SWITCHBODY.stl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]
2026-06-26 added switches
    [10pin.stl, 20260619-BT_SWITCH_HOUSING_chamfered-Box.3mf, 20260619-BT_SWITCH_HOUSING_chamfered-Box.stl, 20260620-BT_SWITCH_HOUSING_chamfered-Box.stl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]
